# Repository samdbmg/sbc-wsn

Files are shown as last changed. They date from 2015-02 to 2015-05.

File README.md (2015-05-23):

# Speckled Bushcricket Wireless Sensor Network
Wireless Sensor Network for Acoustic Monitoring of Speckled Bush Crickets

##Known Issues (Node)
* Assembled sensor node temperature and light level sensors are broken (heat damage possibly)
* Sensor node environment sensors will require creative mounting for light and RH to be exposed outside. Suggest modifying onto an external header to another board (would also solve above problem)

##Known Issues (Base)
* GSM Modem doesn't currently execute HTTP requests, an error returns after setting the URL
* Base unit sometimes doesn't wake up at same time as node. Fitting a crystal to the Discovery board and switching RTC to the external 32k oscillator may help
* Power supplies start and generate stable output, however destroy regulator ICs after Discovery board is connected. Recommend thorough design review
* Discovery board will not fit unless headphone connector and button caps are removed. Suggest reworking to flip board, so Discovery fits on top and modem on bottom

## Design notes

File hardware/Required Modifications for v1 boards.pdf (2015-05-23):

# Required Modifications (Sensor Node v1)

## Radio Pins

- Connect MOSI to switch pin 10
- Connect MISO to switch pin 9
- Additionally, due to lack of soldermask the bottom side of the radio module must be

covered with insulating tape before soldering to avoid short circuiting with the ground plane

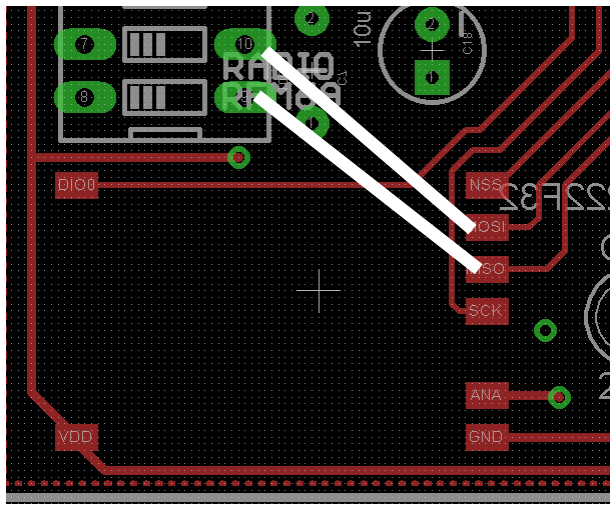
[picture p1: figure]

## LMV551 Op-amp

Cut trace for pins 1,3 and 4, reroute as shown on diagram

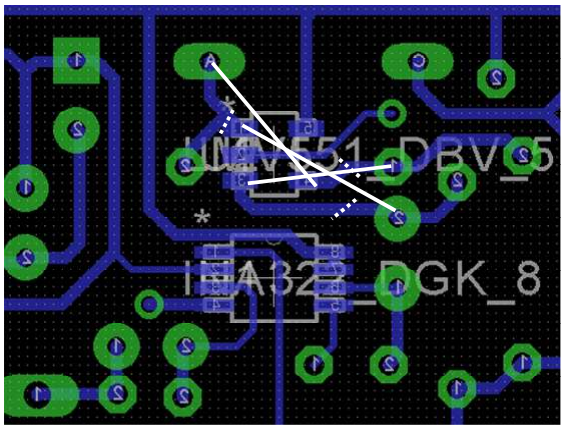
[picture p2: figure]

## Additional Capacitors

Add additional 100u electrolytic and 1u ceramic capacitors across R7. Note that negative is closest to the transducer connector.

Add additional 100u electrolytic to D2 anode (note that D2 is replaced with a resistor below), with negative lead soldered to board ground plane

## Analog Parts

- Replace C4, C1 with 1nf ceramic each
- Replace D2 with 62k
- Replace R10 with 7k5
- Replace R2 with 180k
- Replace R3 with 330k
- Replace R4 with 10k
- Replace R5 with 15k
- Replace R8 with 330k
- Replace R11 with 210k
- Do not fit R6

# Required Modifications (Base Unit v1)

- Do not fit via under SD card slot
- Do not fit R5, R6, R7, R8, R9
- Power supply design is flawed and destroys regulator IC (pins 1 and 2 become shorted) when

connected to Discovery board. Current workaround is to remove regulators, use regulator on Discovery board and a 5V USB source.

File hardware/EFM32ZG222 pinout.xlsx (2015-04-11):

PA0 | A
PA1 | A
PA2 | A
IOVDD_0 | PWR
VSS | PWR
PC0 | C
PC1 | C
PC2 | C
PC3 | C
PC4 | C
LFXTAL_P | PWR
LFXTAL_N | PWR
PA8 | A
PA9 | A
PA10 | A
RESETn | PWR
PB11 | B
VSS | PWR
AVDD_1 | PWR
HFXTAL_P | PWR
HFXTAL_N | PWR
IOVDD_3 | PWR
AVDD_0 | PWR
PD4 | D
PD5 | D
PD6 | D
PD7 | D
VDD_DREG | PWR
DECOUPLE | PWR
PC8 | C
PC9 | C
PC10 | C
PC11 | C
PC13 | C | yeah, pc12 is skipped
PC14 | C
PC15 | C
PF0 | F
PF1 | F
PF2 | F
PF3 | F
PF4 | F
PF5 | F
IO_VDD5 | PWR
VSS | PWR
PE10 | E
PE11 | E
PE12 | E
PE13 | E

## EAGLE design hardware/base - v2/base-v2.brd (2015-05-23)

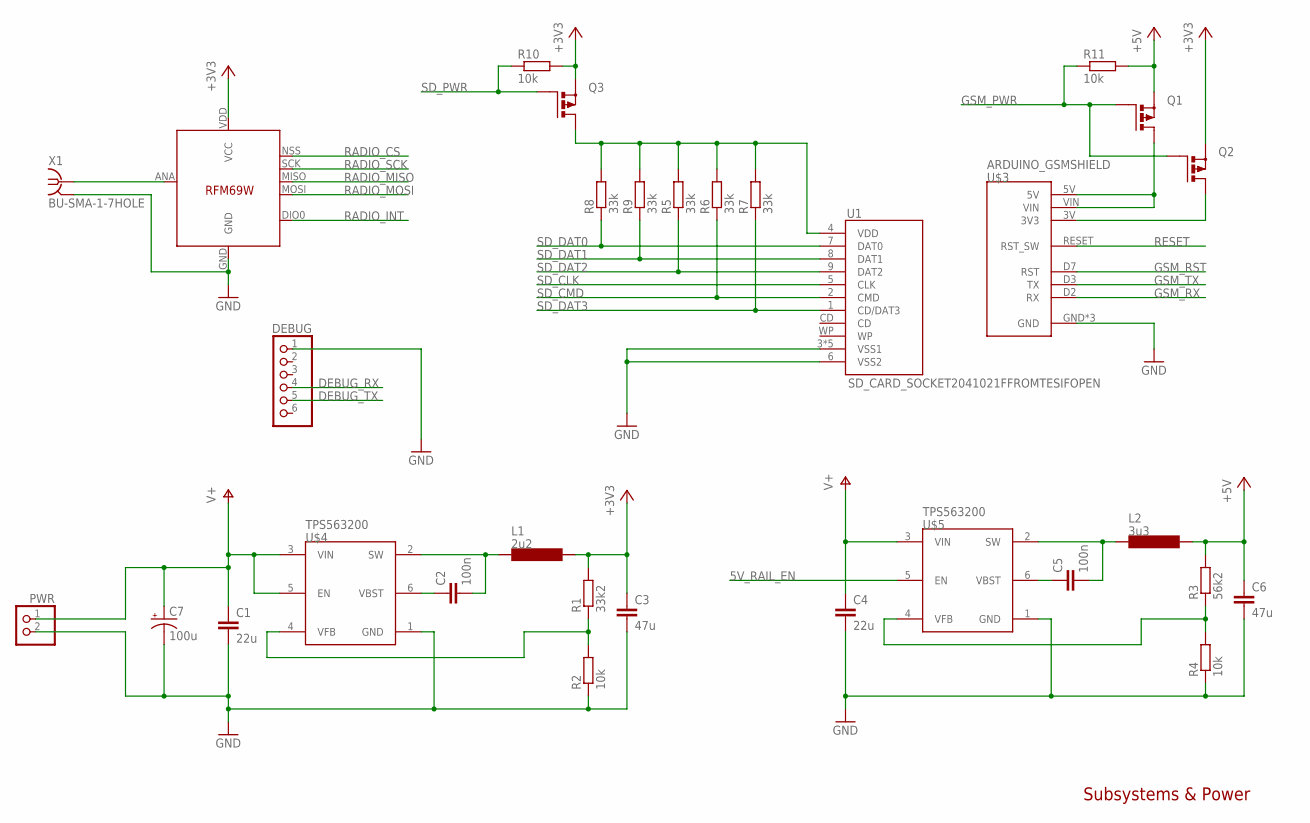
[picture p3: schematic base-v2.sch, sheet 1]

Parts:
C1, C4: 22u; 1206
C2, C5: 100n; CAP-PTH-SMALL
C3, C6: 47u; 1206
C7: 100u; CPOL-RADIAL-10UF-25V
DEBUG: PINHD-1X6; 1X06
L1: 2u2; SRR7032
L2: 3u3; SRR7032
PWR: PINHD-1X2; 1X02
Q1, Q2, Q3: PMOSFET_PTO220BH; TO220BH
R1: 33k2; 0204/7
R2, R4, R10, R11: 10k; 0204/7
R3: 56k2; 0204/7
R5, R6, R7, R8, R9: 33k; 0204/7
U1: SD_CARD_SOCKET2041021FFROMTESIFOPEN; SDCARD_2041021-3
U$2: RFM69; RFM69W-MINPADS
U$3: ARDUINO_GSMSHIELD; ARDUINO-NOHOLE
U$4, U$5: TPS563200; DDC0006A
X1: BU-SMA-1-7HOLE; SMA_1-7HOLES

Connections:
5V_RAIL_EN: U$5.5 (EN); also elsewhere on the board
+3V3: C3.1, L1.2, Q2.S, Q3.S, R1.2, R10.2, U$2.VDD (VCC); also elsewhere on the board
+5V: C6.1, L2.2, Q1.S, R3.2, R11.2; also elsewhere on the board
DEBUG_RX: DEBUG.4; also elsewhere on the board
DEBUG_TX: DEBUG.5; also elsewhere on the board
GND: C1.2, C3.2, C4.2, C6.2, C7.2 (-), DEBUG.1, PWR.2, R2.1, R4.1, U1.3 (VSS1), U1.6 (VSS2), U1.SH1 (VSS1), U1.SH2 (VSS1), U1.SH3 (VSS1), U1.SH4 (VSS1), U$2.GND, U$3.GND, U$3.GND1 (GND), U$3.GND2 (GND), U$4.1 (GND), U$5.1 (GND), X1.2, X1.3 (2), X1.4 (2), X1.5 (2); also elsewhere on the board
GSM_PWR: Q1.G, Q2.G, R11.1; also elsewhere on the board
GSM_RST: U$3.D7 (RST); also elsewhere on the board
GSM_RX: U$3.D2 (RX); also elsewhere on the board
GSM_TX: U$3.D3 (TX); also elsewhere on the board
unnamed: Q1.D, U$3.5V, U$3.VIN
unnamed: Q2.D, U$3.3V (3V3)
RADIO_ANT: U$2.ANA (ANT), X1.1
RADIO_CS: U$2.NSS (SEL); also elsewhere on the board
RADIO_INT: U$2.DIO0; also elsewhere on the board
RADIO_MISO: U$2.MISO; also elsewhere on the board
RADIO_MOSI: U$2.MOSI; also elsewhere on the board
RADIO_SCK: U$2.SCK; also elsewhere on the board
RESET: U$3.RESET (RST_SW); also elsewhere on the board
SD_CLK: U1.5 (CLK); also elsewhere on the board
SD_CMD: R6.1, U1.2 (CMD); also elsewhere on the board
SD_DAT0: R8.1, U1.7 (DAT0); also elsewhere on the board
SD_DAT1: R9.1, U1.8 (DAT1); also elsewhere on the board
SD_DAT2: R5.1, U1.9 (DAT2); also elsewhere on the board
SD_DAT3: R7.1, U1.1 (CD/DAT3); also elsewhere on the board
SD_PWR: Q3.G, R10.1; also elsewhere on the board
SD_VCC: Q3.D, R5.2, R6.2, R7.2, R8.2, R9.2, U1.4 (VDD)
V+: C1.1, C4.1, C7.1 (+), PWR.1, U$4.3 (VIN), U$4.5 (EN), U$5.3 (VIN)
VREG_3_SW: C2.2, L1.1, U$4.2 (SW)
VREG_3_VBST: C2.1, U$4.6 (VBST)
VREG_3_VFB: R1.1, R2.2, U$4.4 (VFB)
VREG_5_SW: C5.2, L2.1, U$5.2 (SW)
VREG_5_VBST: C5.1, U$5.6 (VBST)
VREG_5_VFB: R3.1, R4.2, U$5.4 (VFB)

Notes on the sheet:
Subsystems & Power

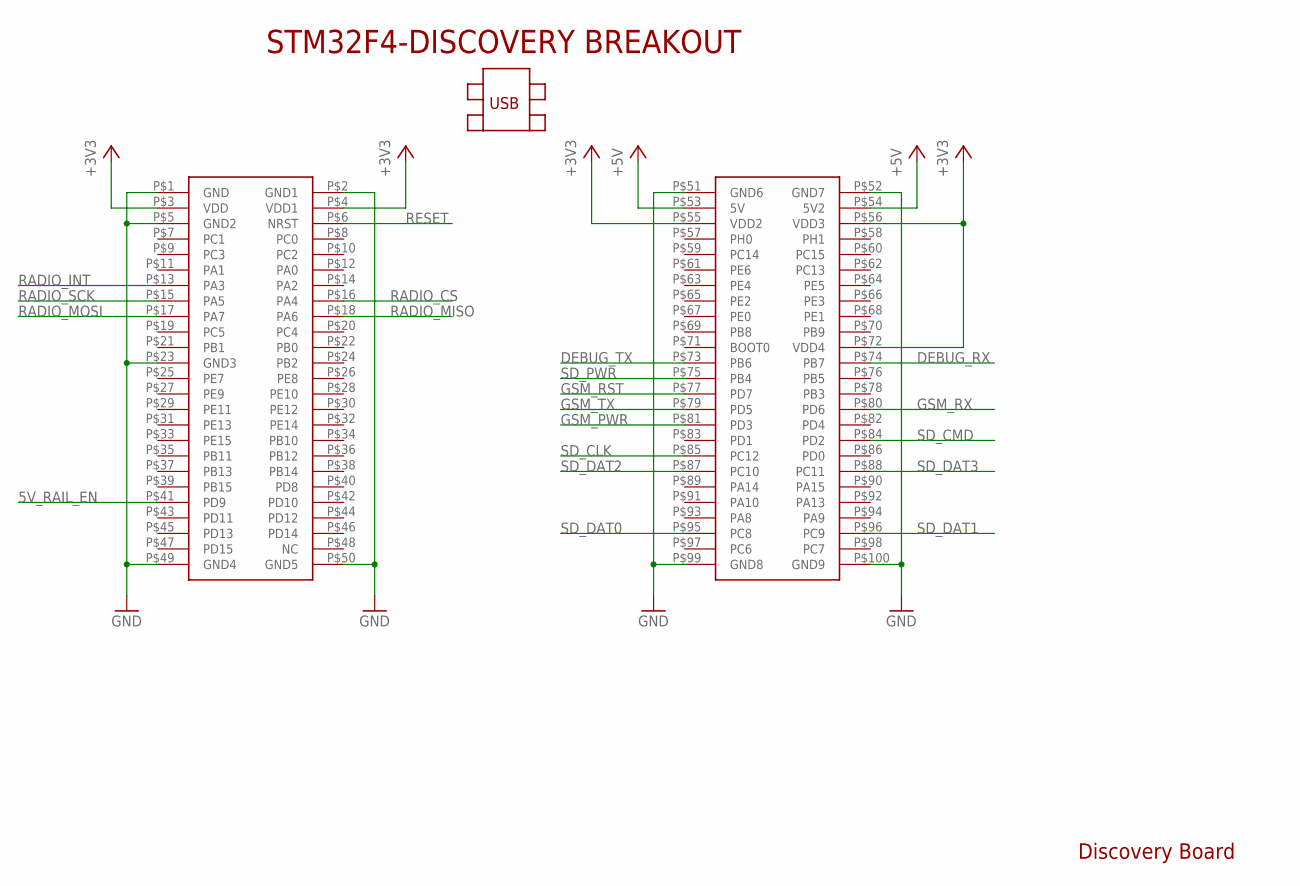
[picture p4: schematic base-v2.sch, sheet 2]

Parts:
U$1: STM32F4-DISCOVERY

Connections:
5V_RAIL_EN: U$1.P$41 (PD9); also elsewhere on the board
+3V3: U$1.P$3 (VDD), U$1.P$4 (VDD1), U$1.P$55 (VDD2), U$1.P$56 (VDD3), U$1.P$72 (VDD4); also elsewhere on the board
+5V: U$1.P$53 (5V), U$1.P$54 (5V2); also elsewhere on the board
DEBUG_RX: U$1.P$74 (PB7); also elsewhere on the board
DEBUG_TX: U$1.P$73 (PB6); also elsewhere on the board
GND: U$1.P$1 (GND), U$1.P$2 (GND1), U$1.P$5 (GND2), U$1.P$23 (GND3), U$1.P$49 (GND4), U$1.P$50 (GND5), U$1.P$51 (GND6), U$1.P$52 (GND7), U$1.P$99 (GND8), U$1.P$100 (GND9); also elsewhere on the board
GSM_PWR: U$1.P$81 (PD3); also elsewhere on the board
GSM_RST: U$1.P$77 (PD7); also elsewhere on the board
GSM_RX: U$1.P$80 (PD6); also elsewhere on the board
GSM_TX: U$1.P$79 (PD5); also elsewhere on the board
RADIO_CS: U$1.P$16 (PA4); also elsewhere on the board
RADIO_INT: U$1.P$13 (PA3); also elsewhere on the board
RADIO_MISO: U$1.P$18 (PA6); also elsewhere on the board
RADIO_MOSI: U$1.P$17 (PA7); also elsewhere on the board
RADIO_SCK: U$1.P$15 (PA5); also elsewhere on the board
RESET: U$1.P$6 (NRST); also elsewhere on the board
SD_CLK: U$1.P$85 (PC12); also elsewhere on the board
SD_CMD: U$1.P$84 (PD2); also elsewhere on the board
SD_DAT0: U$1.P$95 (PC8); also elsewhere on the board
SD_DAT1: U$1.P$96 (PC9); also elsewhere on the board
SD_DAT2: U$1.P$87 (PC10); also elsewhere on the board
SD_DAT3: U$1.P$88 (PC11); also elsewhere on the board
SD_PWR: U$1.P$75 (PB4); also elsewhere on the board

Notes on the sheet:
Discovery Board

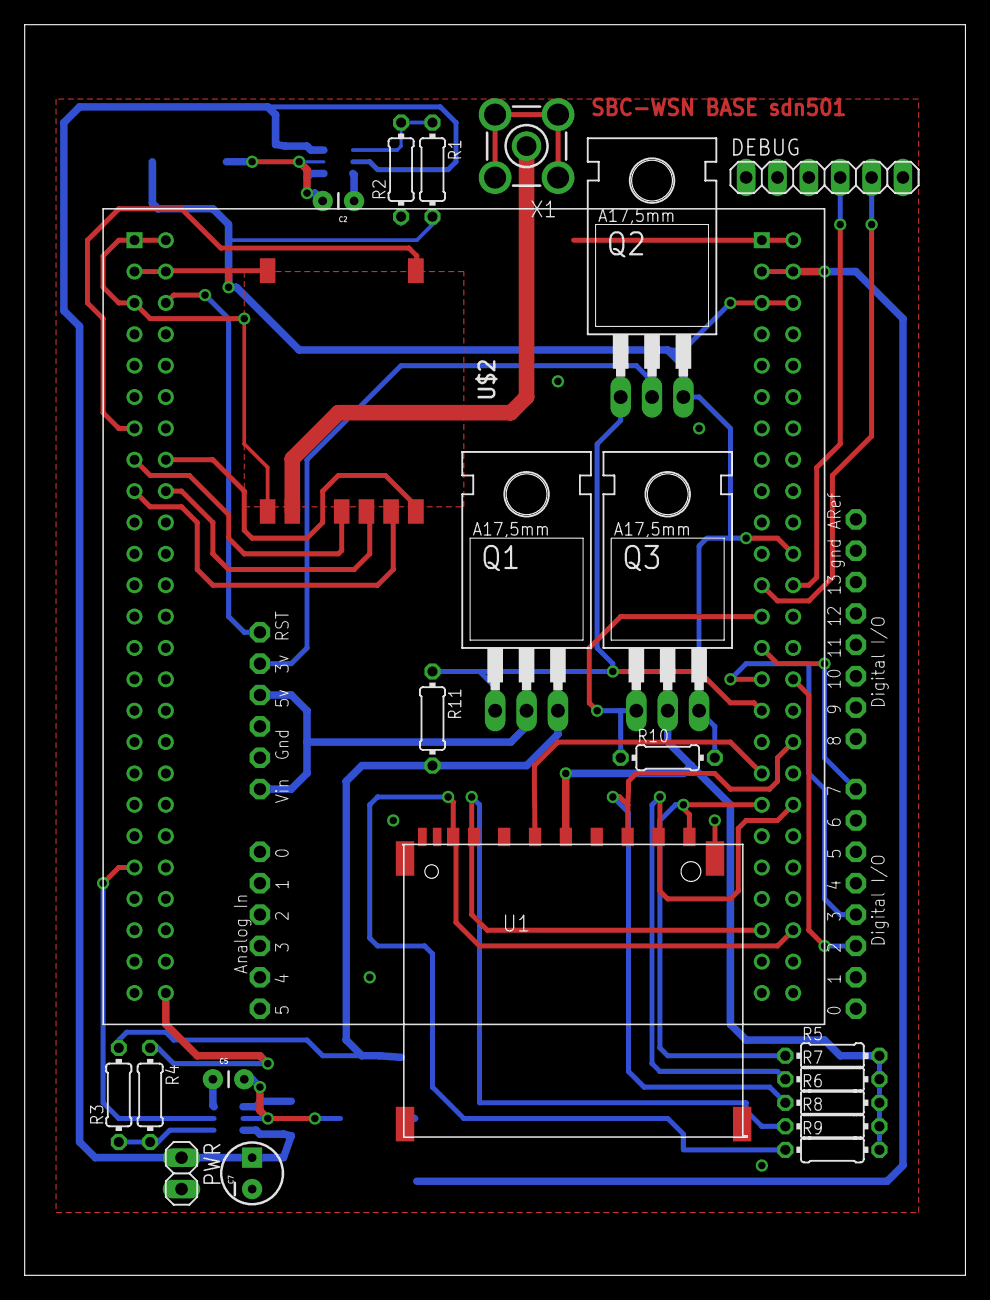
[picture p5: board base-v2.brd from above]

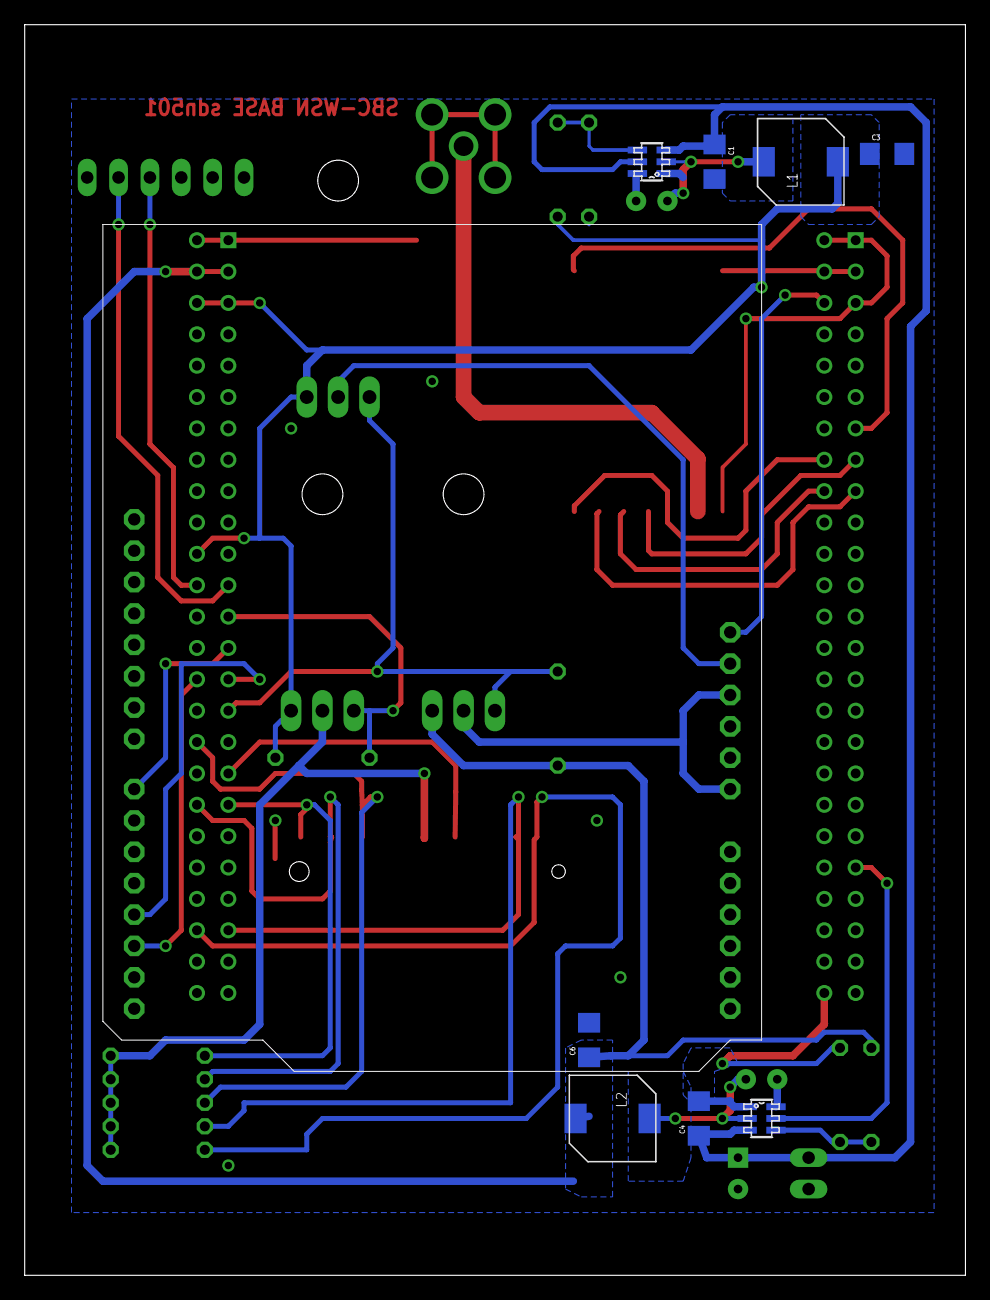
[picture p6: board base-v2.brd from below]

Board: 2 copper layers, 76.2 x 101.3 mm, 32 parts (8 on the bottom side), 34 nets.

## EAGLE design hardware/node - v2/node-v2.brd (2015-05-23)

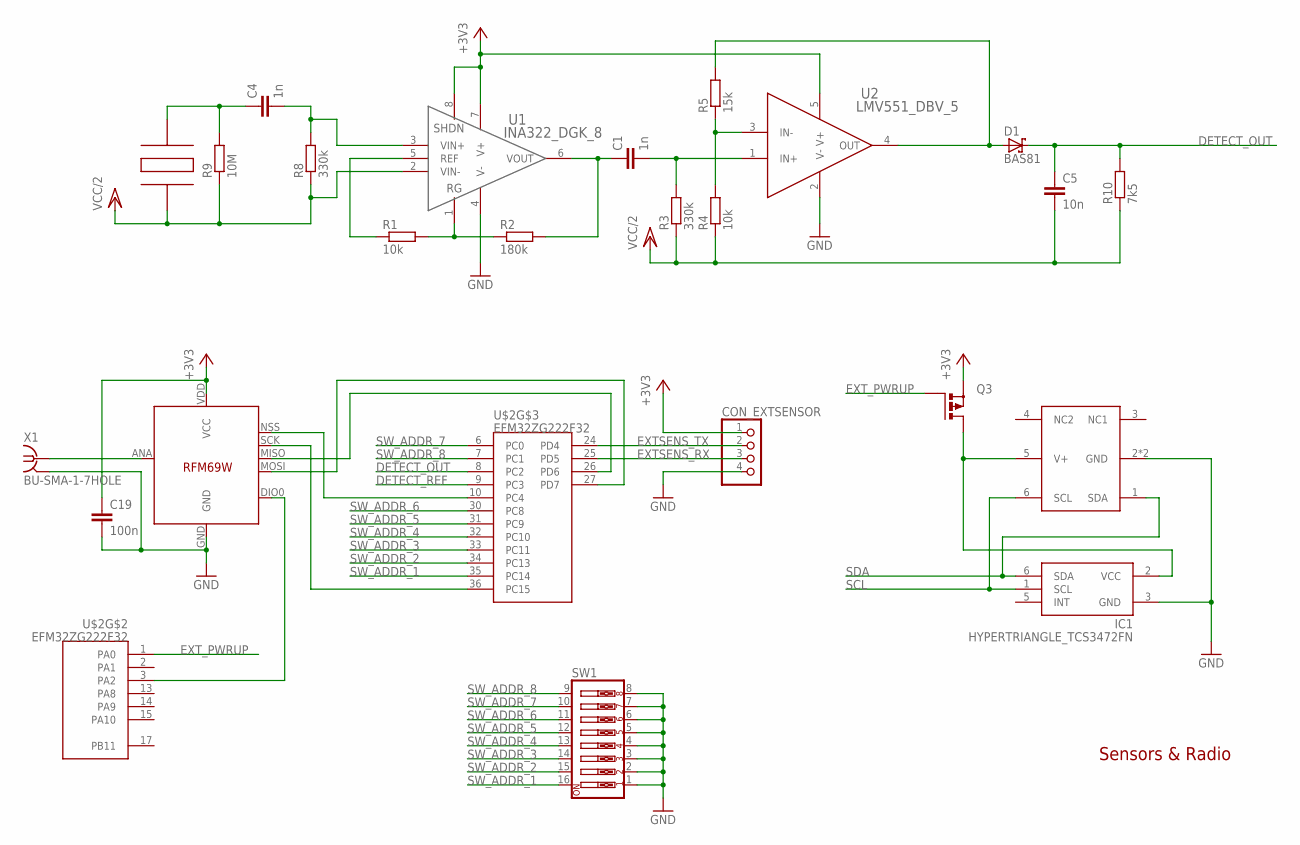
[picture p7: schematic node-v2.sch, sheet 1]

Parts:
C1, C4: 1n; CAP-PTH-SMALL
C5: 10n; CAP-PTH-SMALL
C19: 100n; CAP-PTH-SMALL
CON_EXTSENSOR: PINHD-1X4; 1X04
D1: BAS81; DO35-7
IC1: HYPERTRIANGLE_TCS3472FN; HYPERTRIANGLE_DFN-6
Q3: PMOSFET_PTO220BH; TO220BH
R1, R4: 10k; 0204/7
R2: 180k; 0204/7
R3, R8: 330k; 0204/7
R5: 15k; 0204/7
R9: 10M; 0204/7
R10: 7k5; 0204/7
RADIO: RFM69; RFM69W-MINPADS
SW1: SW_DIP-8; DIPSWITCH-08
U1: INA322_DGK_8; DGK8
U2: LMV551_DBV_5; MF05A
U$1: PIEZOWIREHEADER; 1X02
U$2: EFM32ZG222F32; QFP48
U$3: SHT21
X1: BU-SMA-1-7HOLE; SMA_1-7HOLES

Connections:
+3V3: C19.1, CON_EXTSENSOR.1, Q3.S, RADIO.VDD (VCC), U1.7 (V+), U1.8 (SHDN), U2.5 (V+); also elsewhere on the board
DETECT_OUT: C5.1, D1.C, R10.2, U$2.8 (PC2)
DETECT_REF: U$2.9 (PC3); also elsewhere on the board
EXTSENS_RX: CON_EXTSENSOR.3, U$2.25 (PD5)
EXTSENS_TX: CON_EXTSENSOR.2, U$2.24 (PD4)
EXT_PWRLINE: IC1.2 (VCC), Q3.D, U$3.5 (V+)
EXT_PWRUP: Q3.G, U$2.1 (PA0)
GND: C19.2, CON_EXTSENSOR.4, IC1.3 (GND), RADIO.GND, SW1.1, SW1.2, SW1.3, SW1.4, SW1.5, SW1.6, SW1.7, SW1.8, U1.4 (V-), U2.2 (V-), U$3.2 (GND), U$3.P$1 (GND), X1.2, X1.3 (2), X1.4 (2), X1.5 (2); also elsewhere on the board
INSTR_FILTERED: C1.2, R3.2, U2.1 (IN+)
INSTR_OUT: C1.1, R2.2, U1.6 (VOUT)
unnamed: RADIO.MISO, U$2.26 (PD6)
OPAMP_OUT: D1.A, R5.2, U2.4 (OUT)
OPAMP_VGND: R4.2, R5.1, U2.3 (IN-)
PIEZO_FILTERED: C4.2, R8.2, U1.3 (VIN+)
PIEZO_OUT: C4.1, R9.2, U$1.1 (S+)
RADIO_ANT: RADIO.ANA (ANT), X1.1
RADIO_CS: RADIO.NSS (SEL), U$2.10 (PC4)
RADIO_INT: RADIO.DIO0, U$2.3 (PA2)
RADIO_MOSI: RADIO.MOSI, U$2.27 (PD7)
RADIO_SCK: RADIO.SCK, U$2.36 (PC15)
REFLINE: R1.1, U1.5 (REF)
RGLINE: R1.2, R2.1, U1.1 (RG)
SCL: IC1.1 (SCL), U$3.6 (SCL); also elsewhere on the board
SDA: IC1.6 (SDA), U$3.1 (SDA); also elsewhere on the board
SW_ADDR_1: SW1.16, U$2.35 (PC14)
SW_ADDR_2: SW1.15, U$2.34 (PC13)
SW_ADDR_3: SW1.14, U$2.33 (PC11)
SW_ADDR_4: SW1.13, U$2.32 (PC10)
SW_ADDR_5: SW1.12, U$2.31 (PC9)
SW_ADDR_6: SW1.11, U$2.30 (PC8)
SW_ADDR_7: SW1.10, U$2.6 (PC0)
SW_ADDR_8: SW1.9, U$2.7 (PC1)
VCC/2: C5.2, R3.1, R4.1, R8.1, R9.1, R10.1, U1.2 (VIN-), U$1.2 (S-); also elsewhere on the board

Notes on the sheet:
Sensors & Radio

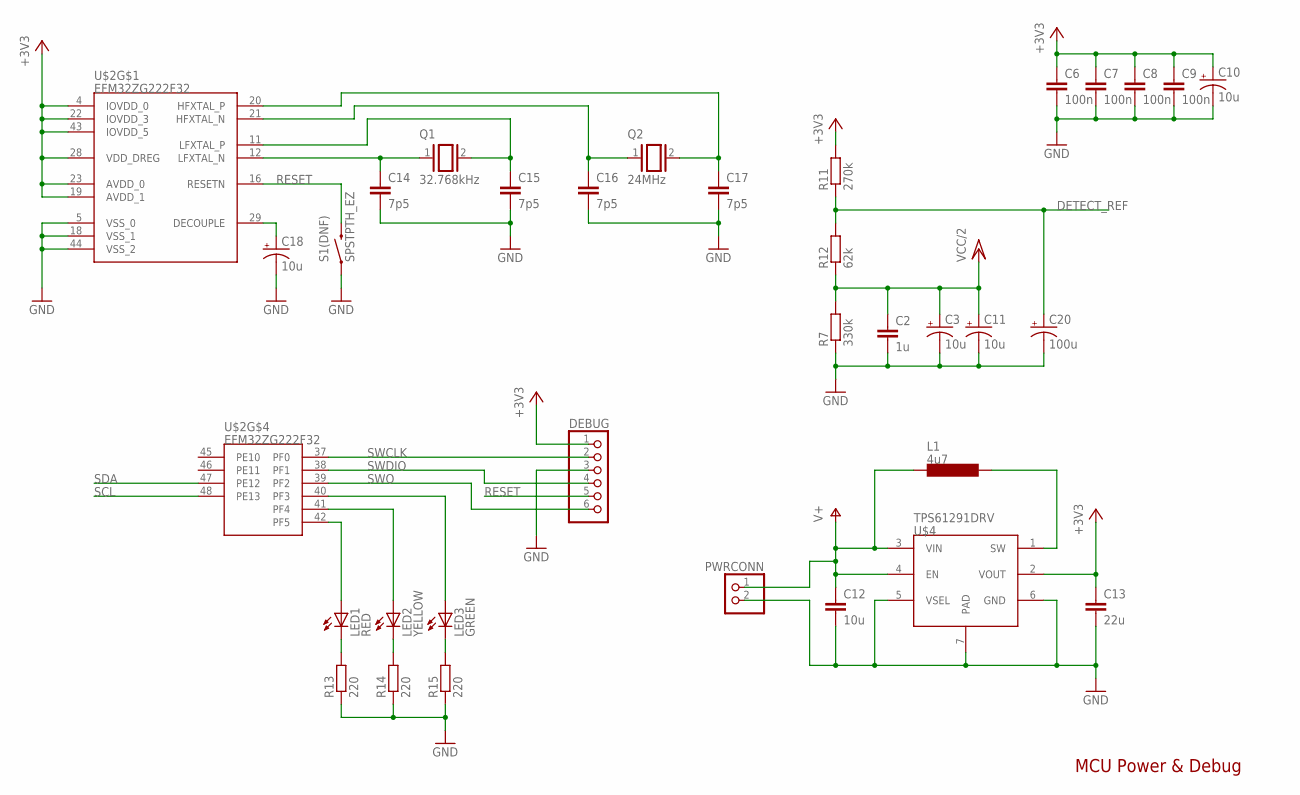
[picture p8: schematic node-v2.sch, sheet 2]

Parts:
C2: 1u; CAP-PTH-SMALL
C3, C10, C11, C18: 10u; CPOL-RADIAL-10UF-25V
C6, C8, C9: 100n; CAP-PTH-SMALL
C7: 100n; CAP-PTH-5MM
C12: 10u; 1206
C13: 22u; 1206
C14, C15, C16, C17: 7p5; CAP-PTH-SMALL
C20: 100u; CPOL-RADIAL-10UF-25V
DEBUG: PINHD-1X6; 1X06
L1: 4u7; LTF5022
LED1: RED; LED3MM
LED2: YELLOW; LED3MM
LED3: GREEN; LED3MM
PWRCONN: PINHD-1X2; 1X02
Q1: 32.768kHz; QS
Q2: 24MHz; QS
R7: 330k; 0204/7
R11: 270k; 0204/7
R12: 62k; 0204/7
R13, R14, R15: 220; 0204/7
S1(DNF): SPSTPTH_EZ; TACTILE-PTH-EZ
U$2: EFM32ZG222F32; QFP48
U$4: TPS61291DRV; DRV0006A

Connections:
+3V3: C6.1, C7.1, C8.1, C9.1, C10.1 (+), C13.1, DEBUG.1, R11.2, U$2.4 (IOVDD_0), U$2.19 (AVDD_1), U$2.22 (IOVDD_3), U$2.23 (AVDD_0), U$2.28 (VDD_DREG), U$2.43 (IOVDD_5), U$4.2 (VOUT); also elsewhere on the board
DECOUPLE: C18.1 (+), U$2.29 (DECOUPLE)
DETECT_REF: C20.1 (+), R11.1, R12.2; also elsewhere on the board
GND: C2.2, C3.2 (-), C6.2, C7.2, C8.2, C9.2, C10.2 (-), C11.2 (-), C12.2, C13.2, C14.2, C15.2, C16.2, C17.2, C18.2 (-), C20.2 (-), DEBUG.3, PWRCONN.2, R7.1, R13.1, R14.1, R15.1, S1(DNF).1, U$2.5 (VSS_0), U$2.18 (VSS_1), U$2.44 (VSS_2), U$4.5 (VSEL), U$4.6 (GND), U$4.7 (PAD); also elsewhere on the board
LED_GREEN: LED3.A, U$2.40 (PF3)
LED_RED: LED1.A, U$2.42 (PF5)
LED_YELLOW: LED2.A, U$2.41 (PF4)
LFXTAL_N: C15.1, Q1.2, U$2.11 (LFXTAL_P)
LFXTAL_P: C14.1, Q1.1, U$2.12 (LFXTAL_N)
unnamed: LED1.K (C), R13.2
unnamed: LED2.K (C), R14.2
unnamed: LED3.K (C), R15.2
RESET: DEBUG.5, S1(DNF).3 (2), U$2.16 (RESETN)
SCL: U$2.48 (PE13); also elsewhere on the board
SDA: U$2.47 (PE12); also elsewhere on the board
SWCLK: DEBUG.2, U$2.37 (PF0)
SWDIO: DEBUG.4, U$2.38 (PF1)
SWO: DEBUG.6, U$2.39 (PF2)
V+: C12.1, L1.1, PWRCONN.1, U$4.3 (VIN), U$4.4 (EN)
VCC/2: C2.1, C3.1 (+), C11.1 (+), R7.2, R12.1; also elsewhere on the board
VREG_SW: L1.2, U$4.1 (SW)
XTALN: C17.1, Q2.2, U$2.20 (HFXTAL_P)
XTALP: C16.1, Q2.1, U$2.21 (HFXTAL_N)

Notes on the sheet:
MCU Power & Debug

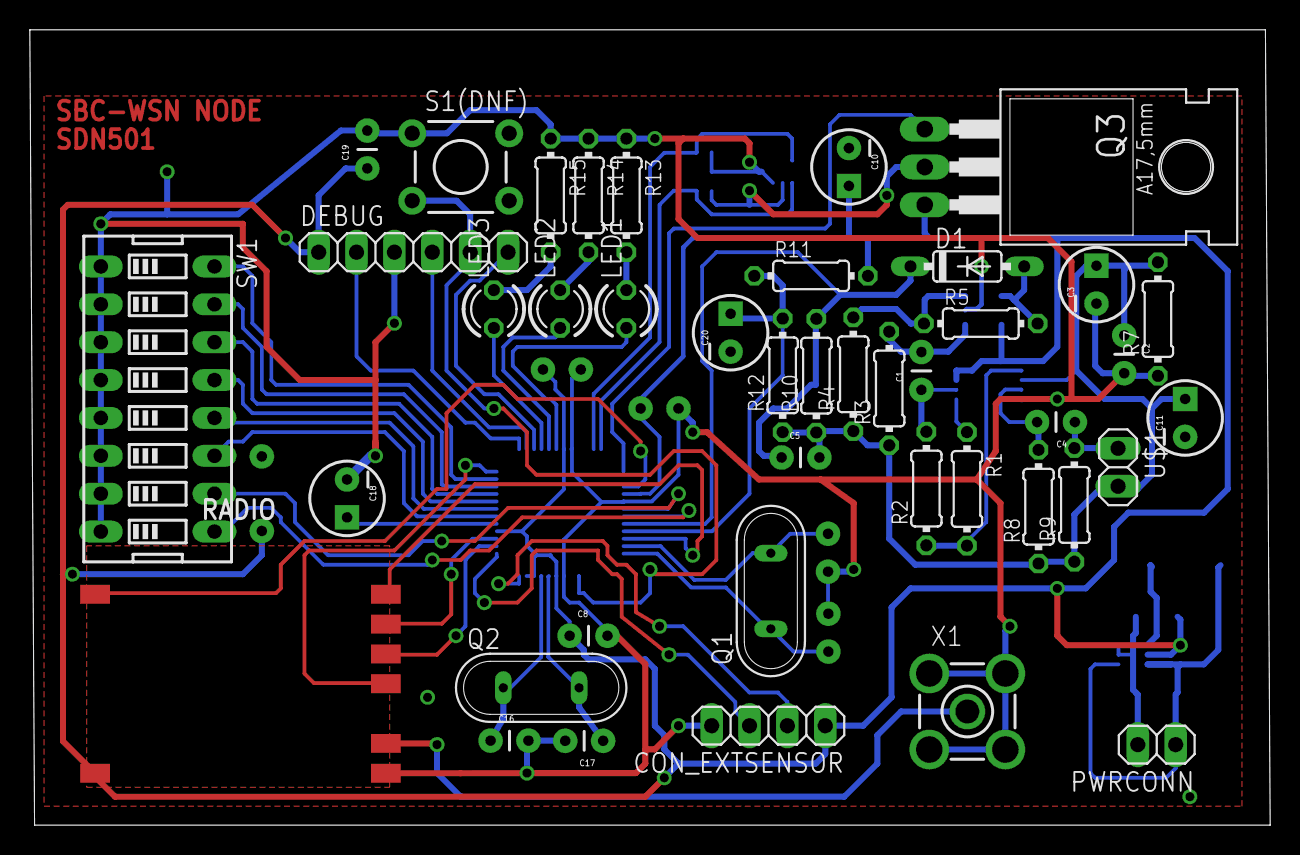
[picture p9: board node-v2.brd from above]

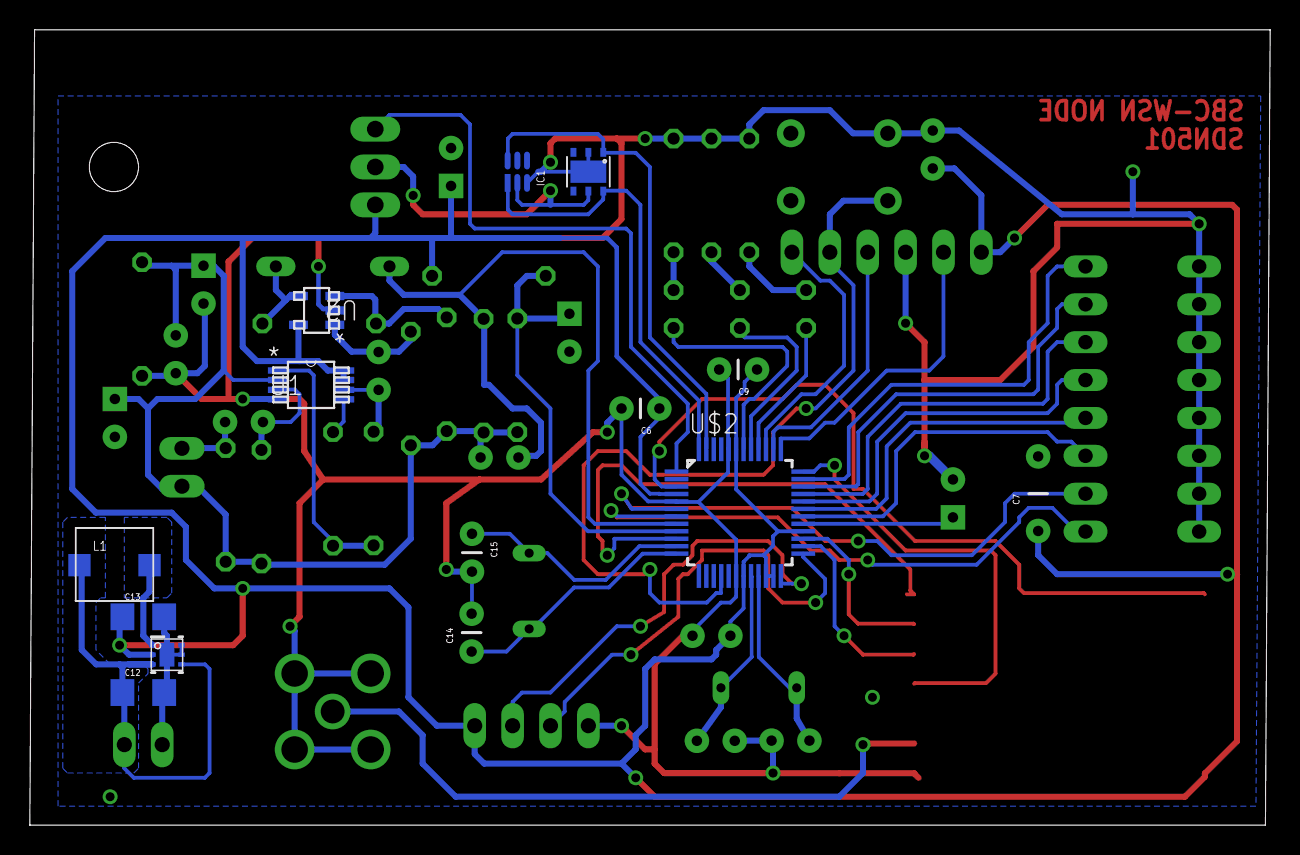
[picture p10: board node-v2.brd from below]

Board: 2 copper layers, 83.2 x 53.3 mm, 56 parts (14 on the bottom side), 50 nets.

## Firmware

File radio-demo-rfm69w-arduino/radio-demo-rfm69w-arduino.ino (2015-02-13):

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
// Please maintain this license information along with authorship
// and copyright notices in any redistribution of this code
// **********************************************************************************

#include <RFM69.h>    //get it here: https://www.github.com/lowpowerlab/rfm69
#include <SPI.h>
//#include <LowPower.h> //get library from: https://github.com/lowpowerlab/lowpower

//*********************************************************************************************
// *********** IMPORTANT SETTINGS - YOU MUST CHANGE/ONFIGURE TO FIT YOUR HARDWARE *************
//*********************************************************************************************
#define NETWORKID     100  //the same on all nodes that talk to each other
#define RECEIVER      1    //unique ID of the gateway/receiver
#define SENDER        2
#define NODEID        RECEIVER  //change to "SENDER" if this is the sender node (the one with the button)
//Match frequency to the hardware version of the radio on your Moteino (uncomment one):
//#define FREQUENCY     RF69_433MHZ
#define FREQUENCY     RF69_868MHZ
//#define FREQUENCY     RF69_915MHZ
#define ENCRYPTKEY    "sampleEncryptKey" //exactly the same 16 characters/bytes on all nodes!
//#define IS_RFM69HW    //uncomment only for RFM69HW! Remove/comment if you have RFM69W!
//*********************************************************************************************

#define SERIAL_BAUD   115200
#define LED           9 //Moteinos have onboard LEDs on D9
#define BUTTON_INT    1 //user button on interrupt 1 (D3)
#define BUTTON_PIN    3 //user button on interrupt 1 (D3)
RFM69 radio;
volatile long i = 0;

void setup() {
  Serial.begin(SERIAL_BAUD);
  Serial.println("Starting");
  radio.initialize(FREQUENCY,NODEID,NETWORKID);
  radio.setPowerLevel(31);
#ifdef IS_RFM69HW
  radio.setHighPower(); //only for RFM69HW!
#endif
  radio.encrypt(ENCRYPTKEY);
  char buff[50];
  sprintf(buff, "\nListening at %d Mhz...", FREQUENCY==RF69_433MHZ ? 433 : FREQUENCY==RF69_868MHZ ? 868 : 915);
  Serial.println(buff);
  Serial.flush();
  pinMode(BUTTON_PIN, INPUT_PULLUP);
  pinMode(LED, OUTPUT);
  attachInterrupt(BUTTON_INT, handleButton, FALLING);
}

//******** THIS IS INTERRUPT BASED DEBOUNCING FOR BUTTON ATTACHED TO D3 (INTERRUPT 1)
#define FLAG_INTERRUPT 0x01
volatile unsigned long mainEventFlags = 0;
boolean buttonPressed = false;
void handleButton()
{
  mainEventFlags |= FLAG_INTERRUPT;
}

byte LEDSTATE=LOW; //LOW=0
void loop() {
  //******** THIS IS INTERRUPT BASED DEBOUNCING FOR BUTTON ATTACHED TO D3 (INTERRUPT 1)
  
  if (mainEventFlags & FLAG_INTERRUPT)
  {
    //LowPower.powerDown(SLEEP_30MS, ADC_OFF, BOD_ON);
    mainEventFlags &= ~FLAG_INTERRUPT;
    if (!digitalRead(BUTTON_PIN)) {
      buttonPressed=true;
    }
  }
  i++;
  
  if (i > 0x2FFFE && digitalRead(BUTTON_PIN))
  {
    i = 0;
    buttonPressed = true;
  }
  
  if (buttonPressed)
  {
    Serial.println("Button pressed!");
    buttonPressed = false;
    radio.send(RECEIVER, "Hi", 2, false); //target node Id, message as string or byte array, message length
      //Blink(LED, 40, 3); //blink LED 3 times, 40ms between blinks
    digitalWrite(LED, !digitalRead(LED));
  }
  
  //check if something was received (could be an interrupt from the radio)
  if (radio.receiveDone())
  {
    //check if received message is 2 bytes long, and check if the message is specifically "Hi"
    if (radio.DATALEN==2 && radio.DATA[0]=='H' && radio.DATA[1]=='i')
    {
      Serial.println("Packet got");
      
      // Auto respond?
      if (!digitalRead(BUTTON_PIN))
      {
        buttonPressed = true;
      }
      
      digitalWrite(LED, !digitalRead(LED));
      Serial.print("   [RX_RSSI:");Serial.print(radio.RSSI);Serial.println("]");
    }
   
    //check if sender wanted an ACK
    if (radio.ACKRequested())
    {
      radio.sendACK();
      Serial.println(" - ACK sent");
      //digitalWrite(LED, !digitalRead(LED));
    }
  }
  
  radio.receiveDone(); //put radio in RX mode
  Serial.flush(); //make sure all serial data is clocked out before sleeping the MCU
  //LowPower.powerDown(SLEEP_8S, ADC_OFF, BOD_ON); //sleep Moteino in low power mode (to save battery)
}

void Blink(byte PIN, byte DELAY_MS, byte loops)
{
  for (byte i=0; i<loops; i++)
  {
    digitalWrite(PIN,HIGH);
    delay(DELAY_MS);
    digitalWrite(PIN,LOW);
    delay(DELAY_MS);
  }
}

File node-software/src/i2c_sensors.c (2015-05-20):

/**
 * Environment sensors interface - header file
 */

/* Standard libraries */
#include <stdint.h>
#include <stdbool.h>

/* Peripheral control headers */
#include "em_device.h"
#include "em_cmu.h"
#include "em_chip.h"
#include "em_gpio.h"
#include "em_i2c.h"
#include "printf.h"

/* Application-specific headers */
#include "i2c_sensors.h"
#include "power_management.h"
#include "misc.h"

#define SENS_TEMP_ADDR 0x40
#define SENS_LIGHT_ADDR 0x29

static bool _sensors_send(uint8_t addr, uint16_t flags, uint8_t txlen,
        uint8_t rxlen);

// Create some storage for I2C transfers
static uint8_t _sens_tx_buffer[3];
static uint8_t _sens_rx_buffer[3];

static I2C_TransferSeq_TypeDef _sens_transfer =
{
        .buf =
        {
            {
                    .data = _sens_tx_buffer,
                    .len = sizeof(_sens_tx_buffer)
            },
            {
                    .data = _sens_rx_buffer,
                    .len = sizeof(_sens_rx_buffer)
            }
        }
};

// Store state of I2C transfer
static volatile bool _sens_i2c_active = false;

/**
 * Configure the sensors and interface
 *
 * @return True on success, false on timeout
 */
bool sensors_init(void)
{
    CMU_ClockEnable(cmuClock_I2C0, true);
    power_set_minimum(PWR_SENSOR, PWR_EM2);

    I2C_Init_TypeDef const i2cInit =
    {
            .clhr = i2cClockHLRStandard,
            .enable = true,
            .freq = 10000,
            .master = true,
            .refFreq = 0
    };

    // Pin configuration
    GPIO_PinModeSet(gpioPortE, 13, gpioModeWiredAndPullUpFilter, 0);
    GPIO_PinModeSet(gpioPortE, 12, gpioModeWiredAndPullUpFilter, 0);

    // Enable pin location
    I2C0->ROUTE = I2C_ROUTE_SDAPEN | I2C_ROUTE_SCLPEN | I2C_ROUTE_LOCATION_LOC6;

    // Enable interrupts
    NVIC_ClearPendingIRQ(I2C0_IRQn);
    NVIC_EnableIRQ(I2C0_IRQn);

    // Enable I2C
    I2C_Init(I2C0, &i2cInit);

    I2C0->CTRL |= I2C_CTRL_AUTOACK | I2C_CTRL_AUTOSN;

    // Configure the light-level sensor to have 10 integration cycles
    _sens_tx_buffer[0] = 0xA0;
    _sens_tx_buffer[1] = 0x01;
    _sens_tx_buffer[2] = 0xF6;
    if (!(_sensors_send(SENS_LIGHT_ADDR, I2C_FLAG_WRITE, 3, 0)))
	{
    	return false;
	}

    // And 4x gain
    _sens_tx_buffer[0] = 0x8F;
    _sens_tx_buffer[1] = 0x01;
    if (!(_sensors_send(SENS_LIGHT_ADDR, I2C_FLAG_WRITE, 2, 0)))
	{
    	return false;
	}

    // And put it back to sleep
    _sens_tx_buffer[0] = 0x80;
    _sens_tx_buffer[1] = 0x00;
    if (!(_sensors_send(SENS_LIGHT_ADDR, I2C_FLAG_WRITE, 2, 0)))
	{
    	return false;
	}

    // Power down until needed
    CMU_ClockEnable(cmuClock_I2C0, false);
    power_set_minimum(PWR_SENSOR, PWR_EM3);

    return true;

}

uint16_t sensors_read(sensor_type_t type)
{
    power_set_minimum(PWR_SENSOR, PWR_EM2);
    CMU_ClockEnable(cmuClock_I2C0, true);

    uint16_t result;
    uint16_t raw_data;

    switch (type)
    {
        case SENS_TEMP:
            // Prepare some instructions
            _sens_tx_buffer[0] = 0xE3;

            // Request temperature
            _sensors_send(SENS_TEMP_ADDR, I2C_FLAG_WRITE_READ, 1, 3);

            // Convert back to a real value
            raw_data = _sens_rx_buffer[1] & 0xFC;
            raw_data |= (((uint16_t)_sens_rx_buffer[0]) << 8);

            // Using formula from datasheet section 6.2, scaled to 100x for
            // avoidance of floating point operations
            uint64_t temp_result = -4685 + (17572 * ((uint64_t)raw_data * 100)) / 6553600;
            result = (uint16_t)(temp_result/100);
            break;

        case SENS_HUMID:
            // Prepare some instructions
            _sens_tx_buffer[0] = 0xE5;

            // Request humidity
            _sensors_send(SENS_TEMP_ADDR, I2C_FLAG_WRITE_READ, 1, 3);

            // Convert back to a real value
            raw_data = _sens_rx_buffer[1] & 0xFC;
            raw_data |= (((uint16_t)_sens_rx_buffer[0]) << 8);

            // Using formula from datasheet section 6.1
            uint32_t humid_result = -6 + (125 * (uint32_t)raw_data) / 65536;
            result = (uint16_t)(humid_result);
            break;

        case SENS_LIGHT:
            // First wake the sensor and start a conversion
            _sens_tx_buffer[0] = 0x80;
            _sens_tx_buffer[1] = 0x03;
            _sensors_send(SENS_LIGHT_ADDR, I2C_FLAG_WRITE, 2, 0);

            // Prepare to read the status register
            _sens_tx_buffer[0] = 0x93;

            // Wait for conversion completion or timeout
            uint8_t attempts = 0;
            while (attempts++ < 3)
            {
                misc_delay(30, true);

                _sensors_send(SENS_LIGHT_ADDR, I2C_FLAG_WRITE_READ, 1, 3);

                if (_sens_rx_buffer[0] & 0x01)
                {
                    attempts = 3;
                }
            }

            // Go and read the data for "clear"
            _sens_tx_buffer[0] = 0xB4;
            _sensors_send(SENS_LIGHT_ADDR, I2C_FLAG_WRITE_READ, 1, 3);

            raw_data = _sens_rx_buffer[0];
            raw_data |= ((uint16_t)_sens_rx_buffer[1]) << 8;

            // Now power down the sensor
            _sens_tx_buffer[0] = 0x80;
            _sens_tx_buffer[1] = 0x00;
            _sensors_send(SENS_LIGHT_ADDR, I2C_FLAG_WRITE, 2, 0);

            result = raw_data;
            break;

        default:
            break;
    }

    CMU_ClockEnable(cmuClock_I2C0, false);
    power_set_minimum(PWR_SENSOR, PWR_EM3);

    return result;
}

/**
 * Fill in and send an instruction to an I2C sensor, wait for it to complete
 * (sleeps when waiting). Don't set rxlen or txlen to be longer than their
 * buffer sizes
 *
 * @param addr  Address of slave I2C sensor. Will be left shifted by 1 for R/W flag
 * @param flags I2C_FLAG_x flags
 * @param txlen Number of bytes from TX buffer to write
 * @param rxlen Number of bytes to read into RX buffer
 * @return		False if command timed out
 */
static bool _sensors_send(uint8_t addr, uint16_t flags, uint8_t txlen,
        uint8_t rxlen)
{
    // Configure transfer parameters
    _sens_transfer.addr = (addr << 1);
    _sens_transfer.flags = flags;
    _sens_transfer.buf[0].len = txlen;
    _sens_transfer.buf[1].len = rxlen;

    // Set transfer flag
    _sens_i2c_active = true;

    // Actually start sending commands
    I2C_TransferInit(I2C0, &_sens_transfer);

    // Delay before attempting wait
    misc_delay(1, true);

    // Set a non-blocking delay as a timeout
    misc_delay(250, false);

    // Wait for transfer completion
    while (_sens_i2c_active)
    {
        power_sleep();

        if (!misc_delay_active())
        {
        	// Timer ran out, exit with failure
        	return false;
        }
    }

    return true;
}

/**
 * Handle the I2C interrupt by triggering another state machine step
 */
void I2C0_IRQHandler(void)
{
    if (_sens_i2c_active)
    {
        I2C_TransferReturn_TypeDef ret = I2C_Transfer(I2C0);

        if (ret != i2cTransferInProgress)
        {
            _sens_i2c_active = false;
        }
    }
}

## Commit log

2015-01-20 EFM32: Refactored to split ADC and pin change mode. Made pin change mode
2015-02-13 RFM69W: Added RFM69W Arduino code
2015-03-04 Added battery power calculator tool
2015-03-05 NODE: Modified how radio powerdown works to actually put radio to low power mode
2015-03-08 NODE: Radio now configures on startup (and responds!). Lights an LED if radio setup fails
2015-03-10 NODE: Radio TX works in principle, some RX skeleton code written. Still needs rest of RX interrupt handler writing, plus configuration data (paying particular attention to ensure listen wake will alw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
2015-03-11 NODE: Made some macros a bit better with brackets courtesy CCL's interviewers
2015-03-11 NODE: Wrote some power management code
2015-03-15 NODE: Improved detect power draw down to 3uA
2015-03-15 NODE: Added some sensor interface code. Doesn't work mind!
2015-03-16 NODE: Ringbuffers made better, config fixed to match Arduino, radios work!
2015-03-16 RFM69W-ARDUINO: Made it work a bit better with Gecko code
2015-03-16 NODE: Remembered how I2C addresses work, fixed temp and RH sensors
2015-03-16 NODE: Finished fixing sensors
2015-03-17 NODE: Some code cleanup as a side effect of using more stringent STM32 compiler, plus made receive mode on radios re-assert if it was active before a transmit started
2015-03-19 NODE+BASE: Added function scheduling and made some power management improvements, prevented nested radio interrupts
2015-04-01 BASE: Added better debugging from an embedded printf() library
2015-04-01 NODE: Added timeout on transmit wait function, made power sleep scheduling slightly more reentrant
2015-04-05 BASE: Fixed a lot of radio protocol bugs, now actually fragments/assembles/ARQs
2015-04-10 BASE: Replaced printf library with one supporting sprintf
2015-04-10 NODEHW: Added schematic for analog bits, EAGLE project
    [node-base.brd, node-base.sch]
2015-04-10 NODEHW: Added MCU power
    [node-base.brd, node-base.sch]
2015-04-10 NODE: Added radio
    [node-base.brd, node-base.sch]
2015-04-10 NODE: Added sensors, power control
    [node-base.brd, node-base.sch]
2015-04-11 NODEHW: Added EFM32 pinout document
    [EFM32ZG222 pinout.xlsx]
2015-04-11 NODEHW: Finished first schematic draft
    [node-base.brd, node-base.sch]
2015-04-11 BASEHW: Schematic mostly done
    [base-base.brd, base-base.sch]
2015-04-13 BASEHW: Added missing power bits, basically done now
    [base-base.brd, base-base.sch]
2015-04-13 NODEHW: Schematic basically finished
    [node-base.brd, node-base.sch]
2015-04-15 NODEHW: Some components placed...
    [node-base.brd, node-base.sch]
2015-04-15 NODEHW: Routeing starts
    [node-base.brd, node-base.sch]
2015-04-15 NODEHW: Routeing ongoing
    [node-base.brd, node-base.sch]
2015-04-15 NODEHW: Routed the switch stuff sortof
    [node-base.brd]
2015-04-15 NODEHW: Routeing rethought, bettered
    [node-base.brd, node-base.sch]
2015-04-16 NODEHW: NODE ROUTING FINISHED!!! YAYYYY!
    [node-base.brd, node-base.sch]
2015-04-17 NODEHW: Tweaks to line up LEDs, fix DRC issues
    [node-base.brd]
2015-04-17 Finished off routeing by fixing some stuff
    [node-base.brd]
2015-04-19 BASEHW: Radio routed
    [base-base.brd]
2015-04-19 NODEHW: PSU layout now looks like TI's
    [node-base.brd, node-base.sch]
2015-04-19 BASEHW: Yayy, hardware design done
    [base-base.brd, base-base.sch]
2015-04-20 BASEHW: Pass for layout bugs, SD pullups
    [base-base.brd, base-base.sch]
2015-04-20 NODEHW: Layout cleanup. Also added base text
    [base-base.brd, node-base.brd]
2015-04-20 NODEHW: Added text label
    [node-base.brd]
2015-04-20 NODEHW: New inductor
    [node-base.brd, node-base.sch]
2015-04-20 BASEHW: New inductors, larger resistors
    [base-base.brd, base-base.sch]
2015-04-21 BASEHW: New SD footprint
    [base-base.brd, base-base.sch]
2015-04-21 NODEHW: Changed transistor package, changed caps to SMD
    [node-base.brd, node-base.sch]
2015-04-21 NODEHW: Sent for fab
    [node-base.brd]
2015-04-21 BASEHW: Replaced PSU caps with 1206 parts, added transistor to make MOSFETs work with VREG
    [base-base.brd, base-base.sch]
2015-04-21 Fixed bad transistor setup
    [base-base.brd, base-base.sch]
2015-04-21 BASEHW: Board sent for MFR
    [base-base.brd]
2015-04-27 NODE: LED Status is now a thing
2015-04-29 Tried to do RTC on discovery board. Doesn't.
2015-05-19 NODE: Added a short delay between sending I2C and waiting for responses, which appears to fix the lockup in sensor setup found with the debugger disconnected (and resulting timing changes). Fixes #5
2015-05-19 NODEHW: Started updates for V2 design
    [node-v2.brd, node-v2.sch]
2015-05-20 NODE: Failure of i2c sensor startup now causes a timeout and an error rather than a lockup. Partially related to #5
2015-05-20 NODEHW: Further updates to capacitor values found as part of #6
    [node-v2.brd, node-v2.sch]
2015-05-22 BOTH: Fixed a radio setup failure bug due to power supply instability
2015-05-22 NODE: Removed test code to upload sample data on radio
2015-05-22 BASE: Now prints out whether a female was detected
2015-05-22 BASE: Added power control for modem, SD card
2015-05-23 BOTH: Tested/fixed schedule generation code (fixes #7) and also fixed RTC alarms (fixes #3) and finally set to name file by current date (fixes #2)
2015-05-23 NODEHW: Completed v2 rework. There are no ADC pins available for #9 therefore it is wontfix.
    [node-v2.brd, node-v2.sch]
2015-05-23 BASEHW: Completed base board rework
    [base-v2.brd, base-v2.sch]

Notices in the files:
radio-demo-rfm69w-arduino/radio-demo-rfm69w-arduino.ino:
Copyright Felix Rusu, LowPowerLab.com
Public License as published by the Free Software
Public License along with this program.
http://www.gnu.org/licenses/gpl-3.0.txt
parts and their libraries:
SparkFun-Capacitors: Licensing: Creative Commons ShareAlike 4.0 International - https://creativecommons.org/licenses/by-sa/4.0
